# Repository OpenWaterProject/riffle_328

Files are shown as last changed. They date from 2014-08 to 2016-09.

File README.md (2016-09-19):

#Welcome!

This is a set of code and instructions for getting started with the Riffle_328 water monitor, version 0.1.8. 

- **QUICK START**.   If you already have experience using Arduino-compatible boards, you should probably just jump to the [Quick Start](https://github.com/dwblair/Riffle-Getting-Started#quick-start) section below to get up and running quickly. In general, the Riffle behaves like an Arduino UNO in the Arduino IDE (you should select "Arduino UNO" as the "Board" in the IDE), but you'll need to install a **special driver** (see [Software prep](test), below) in order to program the device over USB if you're using Mac or Windows.  

- **STEP-BY-STEP**.  If you would prefer more detailed instructions for setting up your Riffle, please check out the [Step-by-Step Instructions](./step-by-step.markdown).

- **EXAMPLES**. If you'd like to try out some example Riffle sensor applications (temperature, pressure, etc) in the [wiki](https://github.com/dwblair/Riffle-Getting-Started/wiki) of this repository (add your own!).

- **DESIGN PHILOSOPHY**.  A brief description of the motivation behind the design of the Riffle can be found [here](https://github.com/OpenWaterProject/riffle/blob/master/design_philosophy.md).  

# How you can contribute

Some useful guidelines about the best way to contribute to the project (or to fork it) can be found [here](contributing.md).

# Support and Licensing 

The Riffle_328 project has been supported through [Public Lab](www.publiclab.org)'s Open Water Initiative, and is licensed under [CERN OHL 1.2](LiCENSE.md).

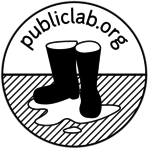
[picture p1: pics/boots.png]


# Quick Overview

**Hardware notes**.  This repository contains the design files and Bill of Materials for the Riffle water monitor.  The Riffle_328 is directly compatible with the Arduino IDE (it can be programmed as an "Arduino UNO" board).  The Riffle_328 ver 0.1.8 has the following features:

- Programmed as an "UNO" in the Arduino IDE
- Uses an Atmel 328p chip, running at 16 MHz and 3.3V.
- On-board microSD card
- On-board Serial-USB conversion using the CH340 chip.
- Battery measurement circuit
- High-precision, temperature-compensated RTC, the DS3221, with a CR1220 backup battery to maintain the time.
- Two power inputs, 3.5 - 6V.  -- one allows for Lithium-Ion charging when the Riffle is plugged into USB, the other is for extended, low-power operation. 
- It has additional on-board EEPROM memory, accessible via the I2C bus.
- It has MOSFET switches that can power down the microSD card, the external sensor power, and the battery measurement circuitry. 
- Analog pins, Digital pins, Power, Ground, Battery voltage, and I2C and SPI buses are broken out on a 2x7 header at the end of the board, as follows:

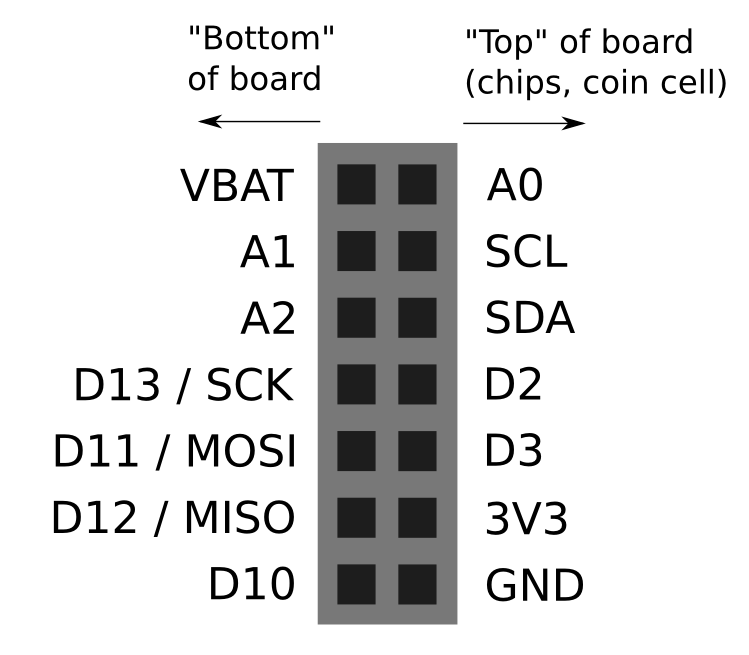
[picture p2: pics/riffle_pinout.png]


**Versions of the Riffle**. [Ben Gamari](https://github.com/bgamari)'s original [Riffle design](https://github.com/bgamari/riffle) is based on an ARM Cortex-M4 chip, the Kinetis K20.  The K20 is a more powerful chip than the Atmel 328, but the K20 version of the Riffle doesn't currently have firmware compatible with the Arduino IDE.  The Riffle_328 design covered in this repository is intended to be as directly compatible with the Arduino IDE as possible.

**Finding more resources**. The Riffle has been developed through many contributions by members of the [Public Lab](http://publiclab.org) community.  For more information, see:

- The main [Public Lab Riffle wiki](https://publiclab.org/wiki/riffle);
- All [posts and research notes](https://publiclab.org/search/riffle) related to the Riffle on Public Lab;
- The [Public Lab Water Quality Mailing list](https://groups.google.com/forum/#!forum/plots-waterquality).

# Quick Start

## Hardware prep

- For basic datalogging, ou'll need a Riffle board, a 3-6 volt battery (3.7 V Lithium Ion battery shown), and CR1220 coin cell battery.  Protoboards (shown) are optional. 

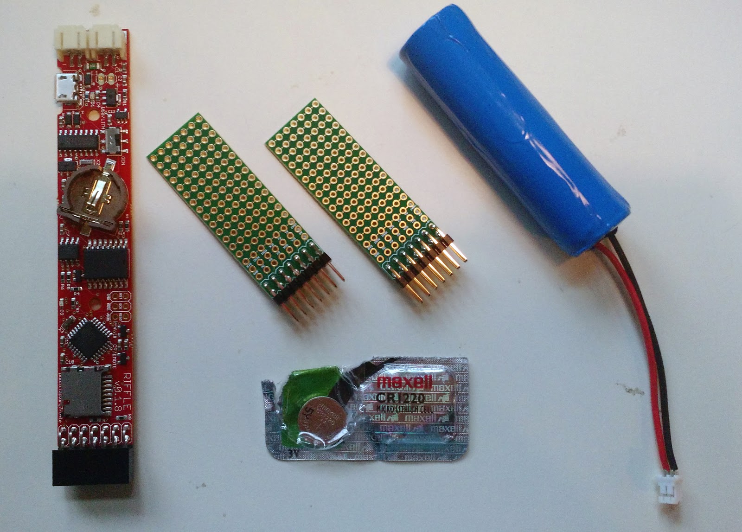
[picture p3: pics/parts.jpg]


- Insert a microSD card and a CR1220 coin cell into the appropriate slots on the Riffle.

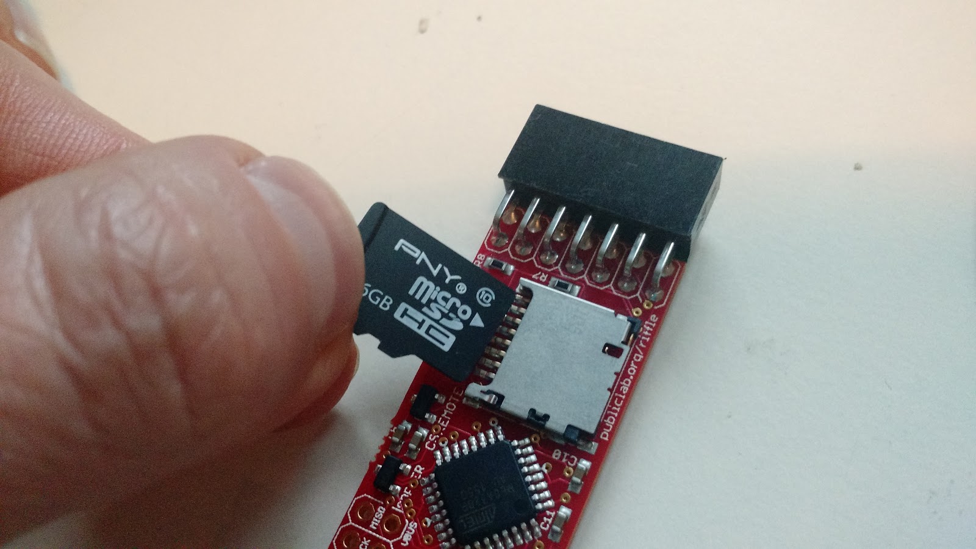
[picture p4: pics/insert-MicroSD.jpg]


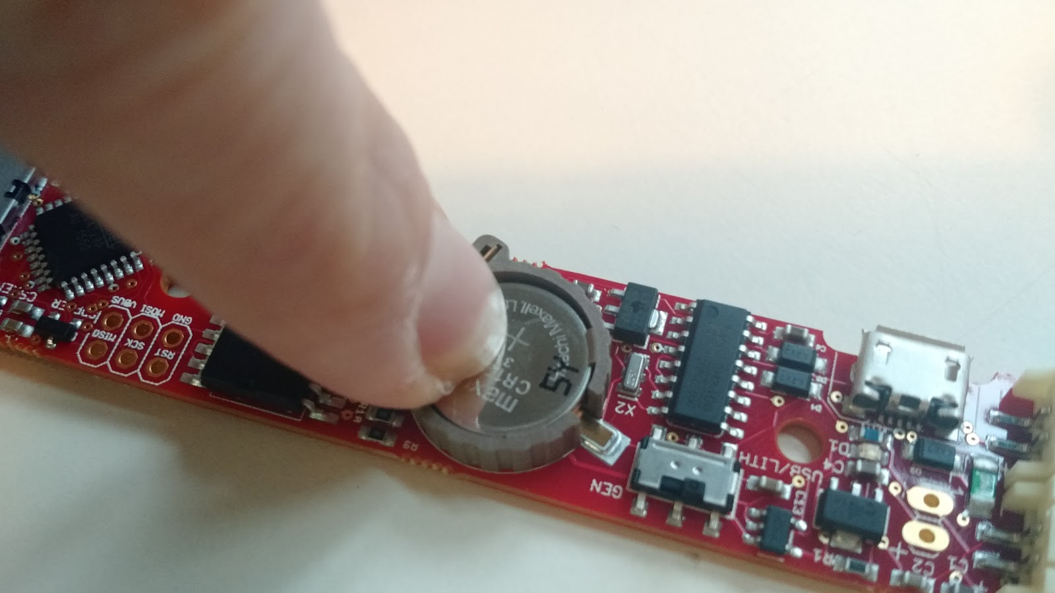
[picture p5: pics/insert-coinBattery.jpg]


- The Riffle 328 ver 0.1.8 has two JST connectors for power inputs, a switch to choose between the two power inputs, and an indicator LED in the middle of the board (connected to pin 9):

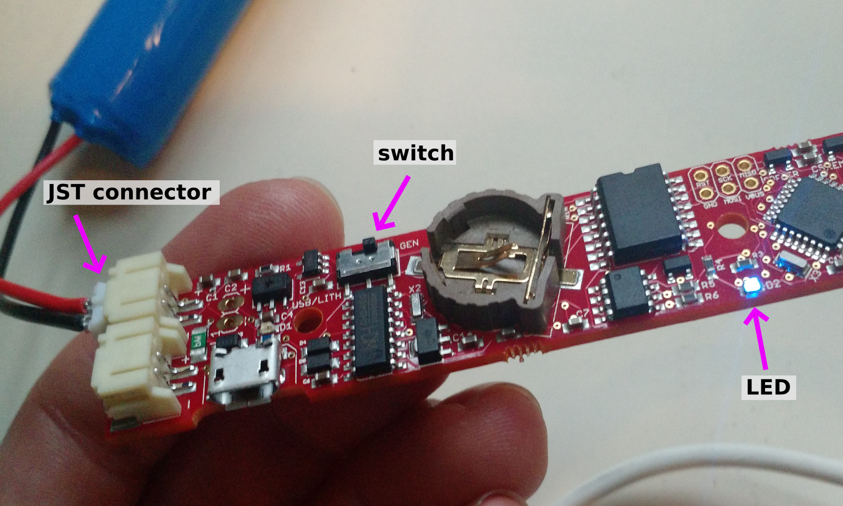
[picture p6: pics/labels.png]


- Insert a lithium ion battery into the 'Lith/USB' JST connector (JST connector labels are on the back side of the board).

- Make sure that the switch on the Riffle is switched to the side labeled 'Lith/USB' (label is next to switch).

- When you're done, your setup should look like this:

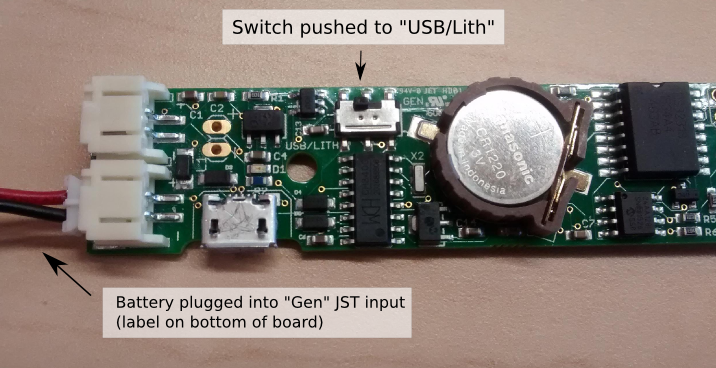
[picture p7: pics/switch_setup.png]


## Software prep

- Make sure that the Arduino IDE (version 1.6.10 or higher) is installed.  If it
 isn't, get it [here](https://www.arduino.cc/en/Main/Software).

- **Installing the USB-Serial Driver**. On Mac or Windows, the Riffle requires a special driver in order to be programmed via the Arduino IDE, due to the onbaord CH340 USB-Serial chip.  For Windows, you can use the driver [here]( http://raysfiles.com/drivers/ch341ser.exe).  For Mac, follow instructions [here]( http://www.instructables.com/id/Arduino-Nano-CH340/). Linux systems should generally not require additional drivers.

- Copy all of the folders in 'arduino_libraries' into the 'libraries' folder inside the 'sketchbook' folder associated with the Arduino IDE install.  These libraries are necessary for running the 'temp_logger.ino' and 'set_rtc.ino' sketches in this repo.  

## Logging values to the microSD card

- Using the Arduino IDE, compile the 'temp_logger.ino' code from the "example_sketches" folder in this repo, and load it onto the Riffle board, using 'Arduino UNO' as the 'Board' version in the Arduino IDE.

- The Riffle should start logging temperature values to the microSD card. These temperature values come from the on-board RTC, and so may be affected by the temeprature of the board (which might slightly higher than ambient temperature, due to the operation of its circuitry). 

- Note: the RTC will have its time set automatically to the system clock when it is programmed via the Arduino IDE.

## Extending the battery lifetime

- Set DEBUG = 0 in temp_logger.ino. This will reduce power by turning off the Serial interface.  It will also mean that the RTC is not set by the System clock.

- Use the 'GEN' JST connector on the Riffle board.  This power input doesn't have a protective diode, thus avoiding a diode-associated voltage drop, and can power the Riffle down to lower battery voltages.

- Test out different microSD cards;  some of them 'sleep' at lower power settings than others.

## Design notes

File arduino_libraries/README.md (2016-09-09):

# Required Arduino Libraries

These libraries must be placed in the 'libraries' folder of your Arduino sketchbook folder.

**Note**:  this snapshot of the libraries is known to work with Riffle 0.1.8.

If you'd like to try updated versions of the libraries (or contribute to bug fixes / development), visit to original libraries below:

- [SdFat](https://github.com/greiman/SdFat)
- [EnableInterrupt](https://github.com/GreyGnome/EnableInterrupt)
- [DS3231](https://github.com/kinasmith/DS3231)
- [LowPower](https://github.com/rocketscream/Low-Power)

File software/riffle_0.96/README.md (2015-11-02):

# Riffle v0.96 Software

Here is the software for the Riffle board version 0.96, which is the production board for the summer of 2015.

## Requirements

### Power Up

The Riffle's brain needs to be on to interact with it. (The "power" led just means there's power to the board, not necessarily that the brain is on. Just slide the switch toward the edge of the board to turn it on.

### Arduino Libraries

The Riffle's Real Time Clock needs a particular flavor of the RTC libarary to be in your Arduino's "Library" folder, which comes via [mizraith's Github page](https://github.com/mizraith/RTClib). Here's what to do:

  - [Download this zip file](https://github.com/mizraith/RTClib/archive/master.zip)
  - Unzip it
  - Remove the "-master" from the folder name so it's "RTClib" instead of "RTClib-master"
  - Move that whole folder into your Arduino "libraries" folder. ([Here is more information](https://learn.sparkfun.com/tutorials/installing-an-arduino-library) on doing that, if you need it.)
  - Restart your Arduino software (also known as the Ardunio IDE).

### USB Driver

The Riffle is using a special USB chip, and may require a special driver so that it is recognized by your computer.

#### Mac OS

For Macs, you'll definitely need a driver. Download and install it from here: [http://raysfiles.com/drivers/ch341ser_mac.zip](http://raysfiles.com/drivers/ch341ser_mac.zip)

#### Ubuntu

If you're using Ubuntu, you don't need anything special.

## Arduino Setup

- Lie to your Arduino software and tell it that Riffle is an "Arduino Uno" in the `Tools > Board` menu.

### Mac OS

- Under `Tools > Serial Port` pick the thing that looks most like: `/dev/tty.wchusbserialXXXX`

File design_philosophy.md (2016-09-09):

# Problem definition
- HOBO datalogger used widely; YSI
- Costs
- Want something extensible
- Something that can connect to the hobby electronics movement
- Use existing code with minimal fuss / muss
- Wanted to make it easy to deploy -- pvc, water bottle, some easy and cheap enclosure
- Easy to share data -- sd card

# Form factor and enclosure
- Wanted to enable water bottle as ‘easiest option’
- Also allows for thin PVC

https://publiclab.org/notes/mathew/02-26-2015/sensors-in-soda-bottles
https://publiclab.org/notes/mathew/01-16-2015/sketching-a-waterproof-pop-bottle-sensor-system

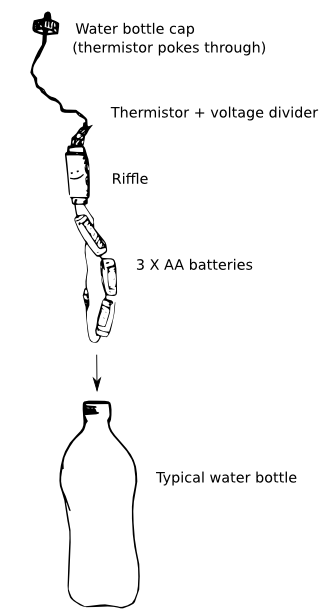
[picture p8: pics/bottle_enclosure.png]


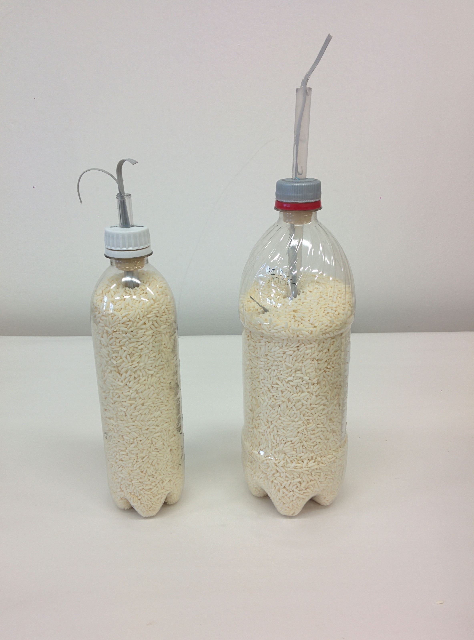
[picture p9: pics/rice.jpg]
 

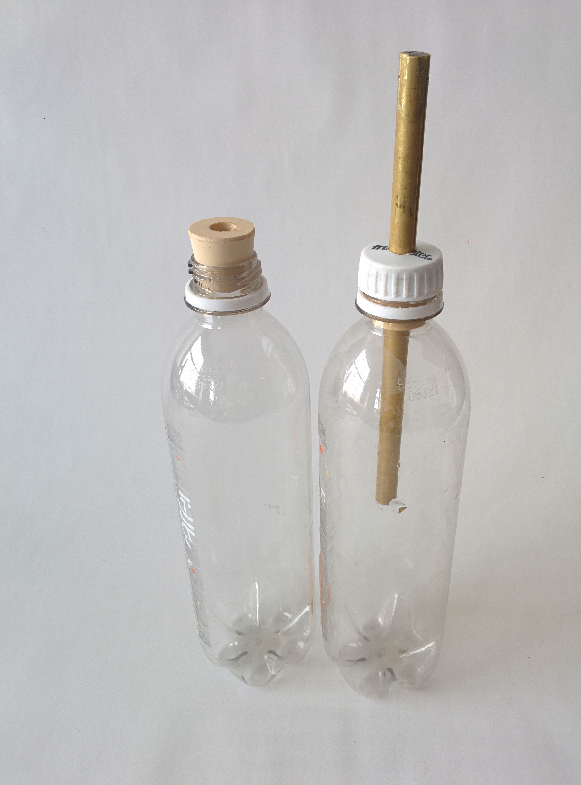
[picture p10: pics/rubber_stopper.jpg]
 

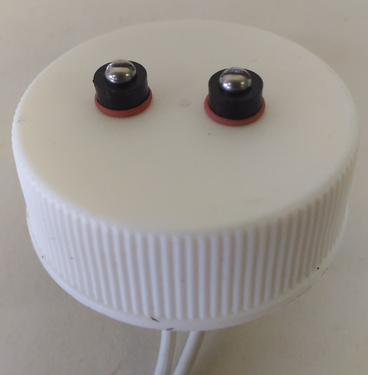
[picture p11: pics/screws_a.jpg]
 

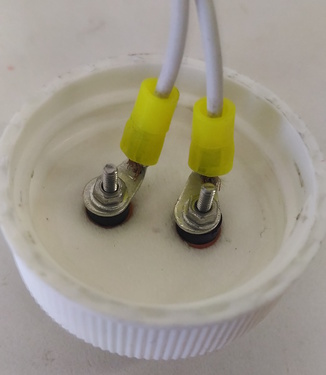
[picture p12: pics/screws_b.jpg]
 

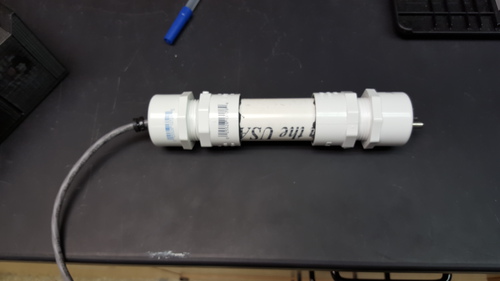
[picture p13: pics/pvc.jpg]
 

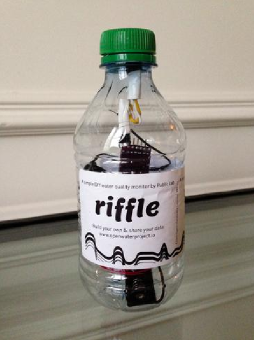
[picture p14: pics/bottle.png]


# What drove IC / placement choices
- Atmel vs ARM
- CH340 -- cheap and easy (but not easy to source)
- DS3231 -- want temp-compensated RTC to line up timestamps
- 2x7 header at end -- to allow water bottle config
- SPI and I2C breakouts at end 
- Hardware interrupts D2 and D3 for any related applications (freq-based measurements like conductivity and depth)
- EEPROM for storing configurations
- Mounting holes for gen purpose mounting

# Power management / choices
- Battery charging circuit
- But requires protective diode to allow for disconnect from USB Serial chip
- So, want to avoid voltage drop
- So, create “gen” battery input, without diode / voltage drop
- RTC alarm functionality 
- Want very low power -- mosfet on external board, mosfet on SD card, mosfet on battery measurement

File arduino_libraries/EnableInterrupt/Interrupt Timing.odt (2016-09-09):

Pin Change Interrupt Timing

an exploration of latency and design

by: GreyGnome (aka, Mike Schwager)

Feb. 8, 2015 v. 1.0

# Introduction

I have a "dirty" switch: it bounces a lot when pressed. The bounces can occur very quickly, on the order of only microseconds apart. This switch is attached to an Arduino Duemilanove, based on the ATmega328p processor. The pin change interrupts on the ATmega chips act only on change of signal (either rising or falling), and they trigger when any pin on a port (== up to 8 pins) is triggered. If you want to determine which pin actually triggered, that would take software and that means a delay from the moment of signal change to determining which pin triggered the change. With a pin change interrupt enabled to trigger on the pin's port, how will a library designed for general use- which must use an algorithm to find the proper pin- react when this switch is pressed?

It bears repeating that for Pin Change Interrupts, the interrupt can take place when any pin on the port is interrupted. This presents a serious design challenge. If you have the luxury of knowing at the time of the signal which pin interrupted, you can design fast, custom code that will react to your simple situation. But remember that we are talking about a library: we don't know which pin may be doing the interrupting. So it must survey the pins to figure out which one(s) changed and had triggered the interrupt. Furthermore, there is an appreciable amount of time that it takes from the moment the triggering event happened to when we enter the interrupt subroutine (ISR) and go through the logic to figure out which pin did the triggering. ...How much time? That I aim to find out.

Why is this a big deal? Think of a bouncy switch: the interrupt triggers, the ISR starts up,

and the first thing we need to do is query the port to see the state of its pins. Well, some time

has elapsed since the triggering event and the query. In the course of that time, it's entirely

possible- and I'm writing this because it's not only possible, but it can happen quite readily-

that the state of the pin changes before we get a chance to sample it. So we get an interrupt but

it looks like a false alarm! The ISR never calls the user's function because none of the user's

interrupt pins appear to have changed.

# The Delay

There is no complete solution to this problem, because of the nature of Pin Change Interrupts and the nature of a general purpose Interrupt SubRoutine (ISR). All you can do is mitigate the situation. I will attempt to do so by capturing the state of the port as early as possible in the ISR. The question is, how early is that?

No matter what, it will take some number of machine instructions from the time of the signal to actually executing the ISR: The current instruction is completed, and there is a jump to the ISR code which takes 3 clock cycles. So that's at least 4 clock cycles, which is about 250 nanoseconds on a 16MHz machine (4 * 62.5 ns). Best theoretical case, then, is that after our signal triggers an interrupt it will take us 250 ns to sample the pin's state. But there's much more than this.

## A General-Purpose ISR Must Save Registers

An interrupt is by definition asynchronous- the computer never knows when it's going to happen. And the compiler writers are not able to know the myriad types of logic that will be necessary inside an interrupt. Thus they can never know which registers may be necessary for a user's ISR, and the implications of that are pretty significant. It means that the first thing the ISR should do is save the values of each and every register of the CPU. ...But isn't that expensive, time-wise? Why yes, yes it is. How so? Here is what the assembly looks like at the beginning of a compiler-generated ISR; note the proper preamble to the ISR pushes all registers (there are reasons registers r2-r17 are not saved for reasons that are not clear to me, but the assembly generated by the compiler for the ISR doesn't use them):

ISR(PORTC_VECT) {

292: 1f 92 push r1

294: 0f 92 push r0

296: 0f b6 in r0, 0x3f ; 63

298: 0f 92 push r0

29a: 11 24 eor r1, r1

29c: 2f 93 push r18

29e: 3f 93 push r19

2a0: 4f 93 push r20

2a2: 5f 93 push r21

2a4: 6f 93 push r22

2a6: 7f 93 push r23

2a8: 8f 93 push r24

2aa: 9f 93 push r25

2ac: af 93 push r26

2ae: bf 93 push r27

2b0: cf 93 push r28

2b2: df 93 push r29

2b4: ef 93 push r30

2b6: ff 93 push r31

The ISR can make no assumptions: What was the state of the CPU when the interrupt took place? What registers are in use by a user's function when called from within the ISR? The compiler is pretty sophisticated, but to ask it to optimize so as to follow a trail of function calls so as to shorten an ISR preamble is beyond its capabilities.

The trouble is in the ISR's function call. In order to allow the library to accept a function call like

enableInterrupt(Pin, function, mode);

where the function's name may not be known at compile time, the ISR must be ready for any eventuality. To not do so means risking bugs by not preserving the main program's registers.

## A Small ISR, for Comparison

So we need our massive preamble. What about an ISR that does not have such restrictions? What if our ISR was simple, and its needs were known to the compiler? To see, I create a small ISR in C:

volatile uint8_t pinstate;

ISR(PORTC_VECT) {

pinstate=PINC;

}

This ISR simply copies the state of Port C to the volatile pinstate variable, which is a memory address accessible by the main program or any function in our sketch. Here is the assembly language that the compiler generates from this C:

volatile uint8_t pinstate;

ISR(PORTC_VECT) {

212: 1f 92 push r1

214: 0f 92 push r0

216: 0f b6 in r0, 0x3f ; 63

218: 0f 92 push r0

21a: 11 24 eor r1, r1

21c: 8f 93 push r24

pinstate=PINC;

21e: 86 b1 in r24, 0x06 ; 6

220: 80 93 60 01 sts 0x0160, r24

}

224: 8f 91 pop r24

226: 0f 90 pop r0

228: 0f be out 0x3f, r0 ; 63

22a: 0f 90 pop r0

22c: 1f 90 pop r1

22e: 18 95 reti

Note that it's much shorter, especially the preamble and the postamble. Much of the code is there because of ISR boilerplate actions:

push r1 Save whatever may be in r1

push r0 Save whatever may be in r0

in r0, 0x3f Store SREG into r0

push r0 Save r0

eor r1, r1 Xor r1 with itself, which is a clever way to put '0'
in r1

How efficient is it? Well we don't need SREG, because the read of port C: in r24, 0x06, and the store of it in memory using the sts 0x0160, r24 don't modify SREG. We don't need to zero out r1, because we never use r1. So all the push'ing and pop'ing are useless in this case, and serve merely to slow us down. Such is life with a compiler vs. hand crafted assembly code. It may be useful to create a hand-crafted ISR in this case.

# Testing Speed

## Entering the ISR

I attempt a test:

A switch is connected as follows: A pin is configured as an input port, and the pullup resistor is on. Pin Change Interrupt is enabled on the pin (which will trigger on any level change). So when I press the switch, the signal goes from high to low and the interrupt is triggered.

My ISR looks (in part) like this; this will turn on and off the Arduino Uno's pin 13 LED:

ISR(PORTC_VECT, ISR_NAKED) {

uint8_t interruptMask;

uint8_t ledon, ledoff;

ledon=0b00100000; ledoff=0b0;

PORTB=ledoff; // LOW

PORTB=ledon; // HIGH

PORTB=ledoff; // LOW

PORTB=ledon; // HIGH

PORTB=ledoff; // LOW

(...)

}

The generated assembly code looks like this:

00000292 <__vector_4>:

ledon=0b00100000; ledoff=0b0;

PORTB=ledoff; // LOW

292: 15 b8 out 0x05, r1 ; 5

PORTB=ledon; // HIGH

294: 80 e2 ldi r24, 0x20 ; 32

296: 85 b9 out 0x05, r24 ; 5

PORTB=ledoff; // LOW

298: 15 b8 out 0x05, r1 ; 5

PORTB=ledon; // HIGH

29a: 85 b9 out 0x05, r24 ; 5

PORTB=ledoff; // LOW

29c: 15 b8 out 0x05, r1 ; 5

Notice a little optimization here: r1 is defined to always contain 0, so we don't even have to load

a value from memory (0 is an important number!). This makes the first out 0x05, r1 command very quick, and by using an oscilloscope we can see just how quickly the chip reacts after receiving the signal:

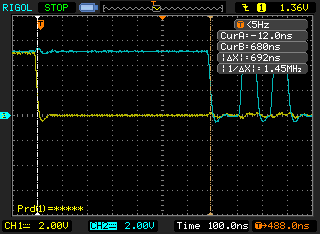
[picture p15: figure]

'.

Look at the two vertical lines on the left and center-right in the above screenshot- those are the cursors. ...So we are measuring 700 nanoseconds from when my switch first closed its connection (yellow trace) to where pin 13 went LOW (blue trace). The cursor lines tell the tale.

How much of that 700 nanoseconds was taken up by the first command itself, the one that signals pin 13? That is:

292: 15 b8 out 0x05, r1 ; 5

In the blue trace, you can see that after I go low I go high, then low, then high again. The second dip- the shorter dip- above, should tell the tale. And it says:

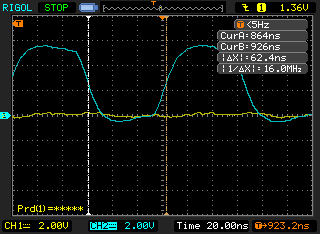
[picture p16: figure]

(note that here I have zoomed in for a closer, more accurate look)

...Lo and behold, the trough- the PORTB=ledoff; is 62.4ns wide, which is equivalent to a 16.0MHz frequency, which is a single clock cycle of the ATmega328p. Note that the data sheet states that the OUT assembly instruction takes 1 cycle. Yay, the stars align!

Now- going back to the first picture: How long did it take to enter the ISR? My experiment measures the time from the switch close to the Pin13 going LOW. We can subtract the time to execute that first command, and get to exactly how long it takes us to enter the ISR:

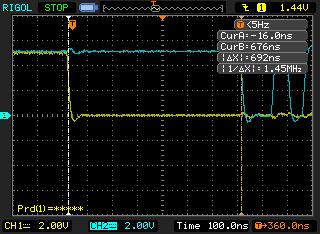
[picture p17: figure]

...That's 692ns measured, or approximately 11 cycles. Minus the 1 cycle that it took our command to run, it takes 10 cycles' time from interrupt to entering the ISR.

Thus, the best response to an interrupt that we could ever hope for is 630ns, more or less. That's at least 630 ns between activation and having a ghost of a chance to query the pins and store their value.

## The Preamble

BUT! Can we just stuff an “in” command at the beginning of the ISR, in order to grab the port's pins' values? Remember, this is a general purpose ISR so the compiler inserts a preamble and a postamble. Here is what the assembly looks like when we don't use NAKED_ISR; note the proper preamble to the ISR (there are reasons registers r2-r17 are not saved; suffice it to say they are scratch and their values are not guaranteed):

ISR(PORTC_VECT) {

292: 1f 92 push r1

294: 0f 92 push r0

296: 0f b6 in r0, 0x3f ; 63

298: 0f 92 push r0

29a: 11 24 eor r1, r1

29c: 2f 93 push r18

29e: 3f 93 push r19

2a0: 4f 93 push r20

2a2: 5f 93 push r21

2a4: 6f 93 push r22

2a6: 7f 93 push r23

2a8: 8f 93 push r24

2aa: 9f 93 push r25

2ac: af 93 push r26

2ae: bf 93 push r27

2b0: cf 93 push r28

2b2: df 93 push r29

2b4: ef 93 push r30

2b6: ff 93 push r31

uint8_t ledon, ledoff;

ledon=0b00100000; ledoff=0b0;

PORTB=ledoff; // LOW

2b8: 15 b8 out 0x05, r1 ; 5

Now let's measure the time from interrupt to shutting off the Pin 13 LED again in that out 0x05, r1 command, just like before. It's given here:

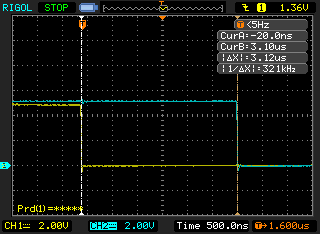
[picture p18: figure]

...yikes! 3.12 microseconds! That's 50 times as long as 62.5 nanoseconds... which means, 50 machine cycles! Well, we do have 17 “push” instructions alone- at 2 cycles each, that's 32 * 62.5ns right there.

This means it would be 3.12 microseconds- at least- from a triggering event, to querying the pins of the PORT, to see which pin triggered. That's painful. Is there anything we can do?

## Query the Port by Hand

There is something: by hand-coding the preamble and post-amble, grab the contents of the port as soon as possible. Here's the code:

ISR(PORTC_VECT, ISR_NAKED) {

uint8_t current;

uint8_t ledon, ledoff;

ledon=0b00100000; ledoff=0b0;

asm volatile("\t"

"push %0" "\t\n\t"

"in %0,%1" "\t\n\t"

: "=&r" (current)

: "I" (_SFR_IO_ADDR(PINC))

);

PORTB=ledoff; // LOW

// in r0, __SREG__ instruction saves SREG, then it's pushed onto the stack.

asm volatile(

"push r1" "\n\t"

"push r0" "\n\t"

"in r0, __SREG__" "\n\t" // 0x3f

"push r0" "\n\t"

"eor r1, r1" "\n\t"

"push r18" "\n\t"

"push r19" "\n\t"

"push r20" "\n\t"

"push r22" "\n\t"

By saving our current PORT state into the variable “current” at the very start of the ISR, using assembly language, we are able to get it as quickly as practicable. Note, however, that because of an SR's special nature we can not be sure if the main code was using the register that will be used for “current” in the “%0” placeholder in the code: “in %0,%1”, above. Therefore, we must push it first... and take care to pop it last at the end of the ISR.

"push %0" "\t\n\t"

"in %0,%1" "\t\n\t"

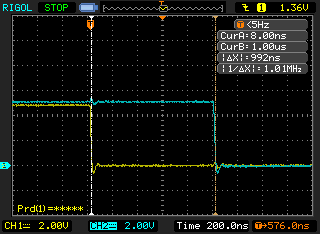
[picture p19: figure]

Now that we have captured our PORT state as soon as possible, we ask: How well did we do? The screen says it took 992 ns... that's about 300 ns slower than a naked ISR preamble, or about 5 cycles. That's close to what we would expect from the assembly code: 2 cycles for the push, 1 for the in, and 1 for the out (to make the LED line go LOW). 4 instructions, or an expected 248ns slower than the routine with the PORTB=ledoff; command first.

...But we're still 62 ns off. What gives? According to my tests, over the course of many runs, there could be some jitter in our interrupt timing. As a matter of fact, there are some significantly longer periods than the one just shown. Take this run for example:

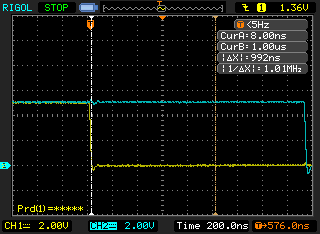
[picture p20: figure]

Here, the two cursors are in exactly the same positions as the previous screenshot.This time it took almost 800ns longer to respond to the interrupt.

This sort of thing happened infrequently, but over the course of a few runs one could find an outlier like this. My feeling is that sometimes the CPU may be in, for example, a timer interrupt and it is unable to service this interrupt until it's done. That's something to keep in mind.

Ultimately, the Pin Change Interrupts are a bit of an oddity. A single interrupt is called for any pin on a port that is triggered, and one needs software if one wants to determine which pin activated. Even then, there's no guarantee that the pin is in the same state that it was when the interrupt was triggered! Caveat programmer- you must be aware of of the capabilities of the hardware that you're working with, and of your system's own performance needs.

That said, I have used a relatively slow Pin Change Interrupt library with great success (http://code.google.com/p/arduino-pinchangeint/). Most cheap switches, for example, are quite bouncy so it's necessary to account for a certain degree of slop in the real world. This is what engineers are paid to do: Make components and systems work in the real world.

And that, my friends, is what they call Rocket Science: It ain't easy.

# A Real Life Example of a Bouncy Switch

## Tracing the Interrupts' Behavior

How well is the ISR grabbing the proper pin state on a fast-changing signal? “Fast” is relative, but for an Arduino running at 16 MHz I would say that fast is anything in the microsecond range. The Arduino's clock runs at a period of 62.5ns which is one machine instruction. In the space of 1 microsecond 16 (1-cycle) machine instructions can run... that's not a whole lot.

In this test, the interrupt library does the following:

1. As soon as we've saved the current PORT state, send out a single pulse.
2. As soon as we've found the pin that on the port that we believe triggered the interrupt, send out a double pulse.

The interesting code parts are these:

ISR(PORTC_VECT, ISR_NAKED) {

uint8_t current;

uint8_t i;

uint8_t interruptMask;

uint8_t ledon, ledoff;

ledon=0b00100000; ledoff=0b0;

asm volatile("\t"

"push %0" "\t\n\t"

"in %0,%1" "\t\n\t"

: "=&r" (current)

: "I" (_SFR_IO_ADDR(PINC))

);

PORTB=ledoff; // LOW

PORTB=ledon; // HIGH

Then:

if (interruptMask & 0x01) {

PORTB=ledoff; // LOW

PORTB=ledon; // HIGH

PORTB=ledoff; // LOW

PORTB=ledon; // HIGH

Now we can see when the interrupt triggers and when it thinks the pin state has changed. How does this line up against our bouncy switch? Are we properly reacting to all the activations?

Here is a real oscilloscope trace of a bouncy switch and of the Interrupt library reacting:

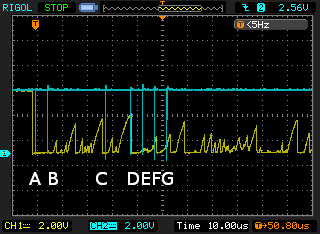
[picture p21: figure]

In this trace, the actions taken by the interrupt library are labelled A through G, in order to easily follow the sequence of events.

Note, again, that this trace shows that the real world is a dirty dirty place. Inside the processor we can be very deterministic, but in the world we have to be aware of what we are dealing with in order to design our systems properly. Here you can see the the bounces are coming microseconds apart; the X-axis time divisions are 10 microseconds. There are some significant pulses that appear less than 10 microseconds apart.

So let's evaluate the actions of the switch and the interrupt library, using that screenshot as our guide...

## Pulses A and B

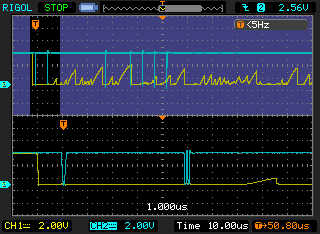
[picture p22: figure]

Zooming in on the two pulses, we see the library behave as expected: The switch (yellow trace) triggers the interrupt (blue trace) which reacts about 1us later. Then, about 5us later, the code has determined which pin activated so if you look closely at the bottom trace you can see that it sends a double-pulse (if you can't see it, you'll just have to trust me). Oll Korrect.

At this point, we have saved the current state of the pins into the portSnapshot variable: When the interrupt activates next, we'll need to know which pin changed from this activation of the interrupt.

The pin's state is saved at a LOW level.

## Pulse C

This is interesting; Pulse C is on the left at the bottom zoomed-in view:

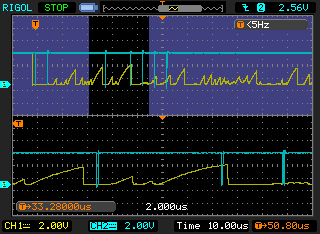
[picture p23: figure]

The interrupt is activated by the rising waveform on the left (note that the ATmega328's circuitry actually activated the interrupt somewhere inside this sawtooth). This would be a change in the pin's state, however, by the time the interrupt reacts, the pin is at a low level (refer to the leftmost pulse in the blue trace at the bottom of the above screenshot). In variable “current”, then, the pin's state is LOW. “current” and the portSnapshot variable would thus look the same, the ISR believes that no pin has activated, and there is no activation of the user's function; there is no double pulse.

Then, about 10 microseconds to the right of Pulse C, we find:

## Pulse D and E

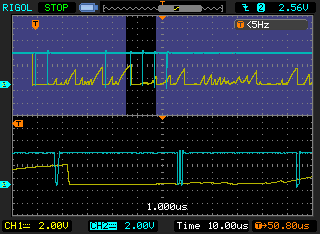
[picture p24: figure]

Pulse D is the leftmost pulse on the bottom trace in the screenshot. Here again we see an activation on a rising pulse, but this rise is appreciably longer than Pulse C. Somewhere during the rise, the ATmega328 recognizes the rising signal, the interrupt triggers, and the library captures the state of the port. This is important: because the ISR has time to recognize the HIGH level (note that the single pulse occurs while the sawtooth wave is still high, so “current” stores this HIGH level), there will be a change in the pin from what was previously saved in the “portSnapshot”. Again if you look closely you can see the double-pulse about 5 microseconds after the initial ISR pulse.

The pin change is recognized and the portSnapshot stores HIGH level.

## Pulse F and G

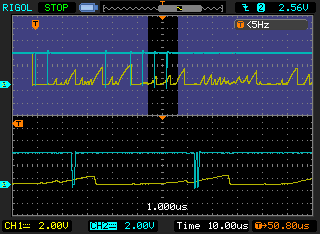
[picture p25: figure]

Here we have an interrupt seemingly out of nowhere; about 5 microseconds after Pulse E comes Pulse F, a single pulse signifying entry of the ISR again. But there is no signal (yellow trace) to activate this ISR! ...Or isn't there?

Remember that the ISR at Pulse D acted on a HIGH transition. However, very soon after the ISR's first pulse we saw the signal transition rapidly to low. The ATmega328 recognized this transition, and tripped the PCIFx register (specifically, here, it's PCIF1): it sets a flag to let the system know there is a pending interrupt. We couldn't act on the interrupt until the previous interrupt exited. However, once it did, we enter the ISR again. This was about 5 microseconds in total after executing the user's function in the previous ISR (which happens to be this:

volatile uint16_t interruptCount=0;

void interruptFunction() {

interruptCount++;

}

). All the register pop's at the end of the ISR, the return to the main program, executing a single instruction in the main program (this is guaranteed by the system), and the return to the ISR had taken 5 microseconds. Note that because the Pin Change Interrupts are high-level interrupts and there are no other interrupts set in this very simple system, we don't have to be concerned about another interrupt having used any of those 5 microseconds (see page 58 of the ATmega48A/48PA/88A/88PA/168A/168PA/328/328 datasheet).

So, to recap: During the ISR that acted on Pulse D, we flagged another interrupt due to the transition from HIGH to LOW. “portSnapshot” would have had registered HIGH for this pin, and now in the ISR for Pulse E “current” registers LOW for this pin. Thus, we find the changed pin and execute the users' interrupt routine at Pulse G.

# Implications

At the start of the Arduino sketch, prior to any switch activations, “current” shows a high value for our pin. We have seen at Pulse C that it's possible for us to miss a transition. Is it possible for us to miss a switch activation?

In the current circuit, we have essentially an RC circuit to V+ but a direct connection to ground. This would explain the sawtooth nature of the waveforms in the switch bounces:

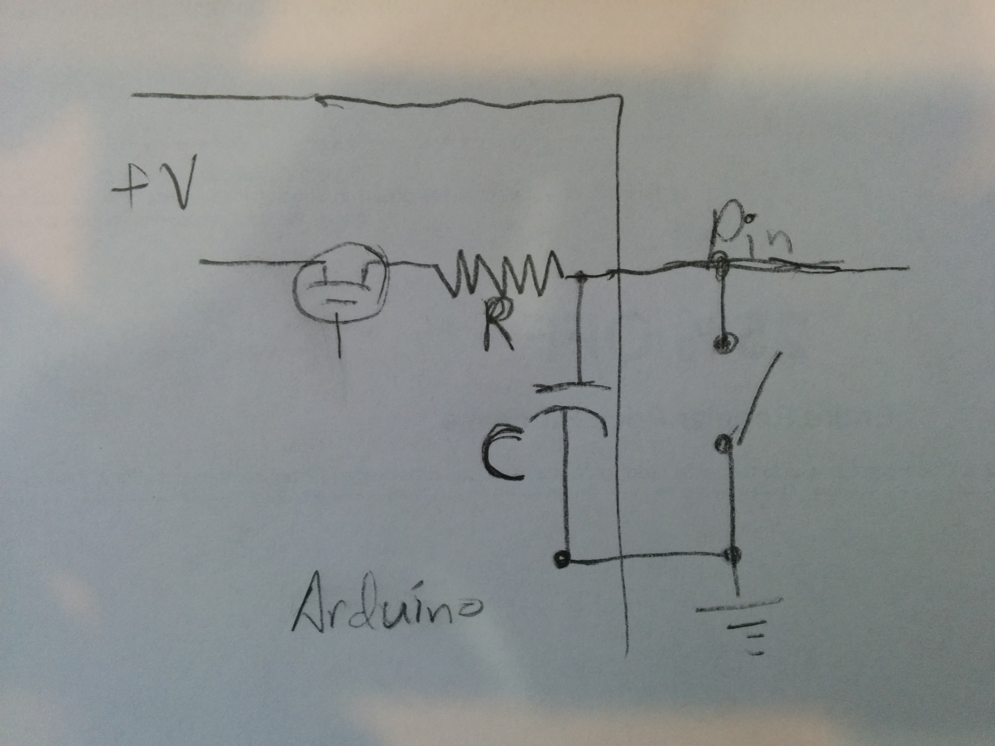
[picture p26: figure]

Because of the longer rise time of the signal when the switch is open, when the initial trigger takes place the signal goes low quickly, but it takes some time to go back to high when it bounces. So the “current” variable is likely to report LOW. So we should see the transition, and record it properly.

However there is no guarantee, and we have not even taken into consideration other interrupts that may be set. If a fast-changing signal on a pin registers a transition (on any Pin Change Interrupt pin) while an ISR is being executed, there is a good possibility that that pin's state will be misread. This makes Pin Change Interrupts a poor choice for fast-acting signals unless fault tolerance is built in to the software, and possibly even problematic in systems with a number of bouncy switches.

Again, however, multiple cheap bouncy rotary encoders have been used satisfactorily by the author with Pin Change Interrupts on the Arduino with an ATmega328p chip. The situation is not dire by any means, but again as always, Caveat Engineer; you must understand your system that is built on compromise- including, that is, the Pin Change Interrupts- and design accordingly.

# EnableInterrupt and PinChangeInt Comparison

This report was written during development of the EnableInterrupt library. The author has maintained another Pin Change Interrupt library, called PinChangeInt https://code.google.com/p/arduino-pinchangeint/. This sort of speed analysis and optimization was not performed for that library. There the compiler and system's code were accepted and measured but not criticized.

So how does this library's speed compare? Is the Enable Interrupt library a significant performance upgrade? Let's compare the two.

## Sketch

For this sketch, we're going to use a software interrupt. The idea is this:

1. Use Port C's 0-bit, which would be Pin A0 on the Arduino Uno, for the software interrupt.
2. Set A0 and Pin 13 high.
3. Print something to indicate start.
4. 2 seconds later, bring A0 low. This will interrupt the system and enter the ISR. The ISR is very simple; the function it calls is a simple variable increment.
5. However, it's a little tricky: We discover by trial-and-error that the interrupt code is not entered immediately. In the main loop, we toggle Pin 13 repeatedly. A little experimentation allows us to create exactly the series of instructions needed so that the pin LOW instruction is the last one run prior to entering the ISR. Thus we can see the LOW called jut before entering the ISR, then observe the HIGH transition performed as the first instruction after the ISR.
6. This will tell us within a couple of machine instructions' time (ie, 130 ns), the exact duration of the ISR.

Here's the loop() code:

void loop() {

uint8_t led_on, led_off; // DEBUG

led_on=0b00100000; led_off=0b0;

//*led_port|=led_mask; // LED high

PORTB=led_on;

PORTC=0x01;

Serial.println("---------------------------------------");

delay(2000); // Every 2 seconds,

PORTC=0x00; // software interrupt, port A0, triggers the ISR

PORTB=led_on;

PORTB=led_off;

PORTB=led_on;

PORTB=led_off; // at this point, we enter the ISR

PORTB=led_on; // this is after the ISR.

Here are the graphs showing the response of the system.

## EnableInterrupt

Here we see the interrupt (yellow line) and the main loop operating, until the ISR takes over and prevents the Pin 13 toggle back to on:

PORTC=0x00; // software interrupt, port A0, triggers the ISR

PORTB=led_on; // We don't see this as the pin is already HIGH

PORTB=led_off;

PORTB=led_on;

PORTB=led_off; // at this point, we enter the ISR

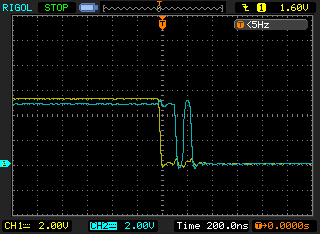
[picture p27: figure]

So it takes 4 machine instructions to enter the ISR.

Following

PORTB=led_off; // at this point, we enter the ISR

in the main loop Pin 13 is brought high again and it stays high until after the next interrupt:

PORTB=led_on; // this is after the ISR.

So we should be able to see exactly when the ISR exits and we can measure the duration of the entire ISR. Here is the graph:

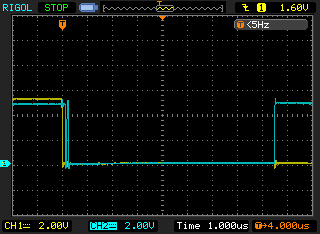
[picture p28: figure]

The ISR thus takes about 8 microseconds.

Compare the PinChangeInt library:

## PinChangeInt

It takes about the same time to enter the ISR, as expected. There is no difference between entering any ISR, that is up to the system (note that the time/div is twice as long here as the previous graph):

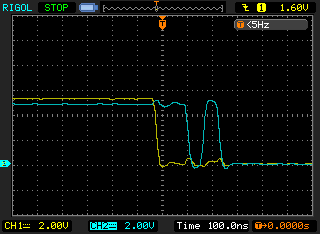
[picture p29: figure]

How long does this ISR take? The graph tells the tale:

Here we can see that, between the execution of these two commands:

PORTB=led_off; // at this point, we enter the ISR

PORTB=led_on; // this is after the ISR.

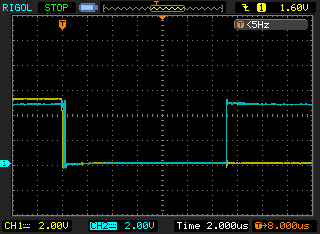
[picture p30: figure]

is about 13 microseconds elapsed time. All else being equal, the Enable Interrupt code is 5 microseconds faster.

# License

Copyright 2015 by Michael Anthony Schwager.

(http://creativecommons.org/licenses/by-sa/2.0/)
This work is licensed under a Creative Commons Attribution-ShareAlike 2.0 Generic License (http://creativecommons.org/licenses/by-sa/2.0/).

Page 12 Copyright 2015 Michael Anthony Schwager. This work is licensed under a Creative Commons Attribution-ShareAlike 2.0 Generic License (http://creativecommons.org/licenses/by-sa/2.0/)

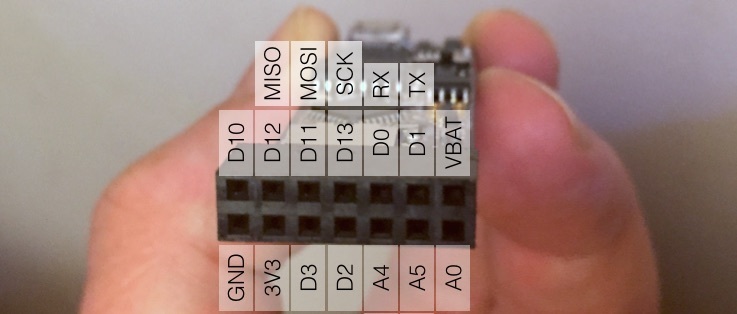
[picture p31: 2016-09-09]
pics/medium_riffle_pinouts_detail.jpg

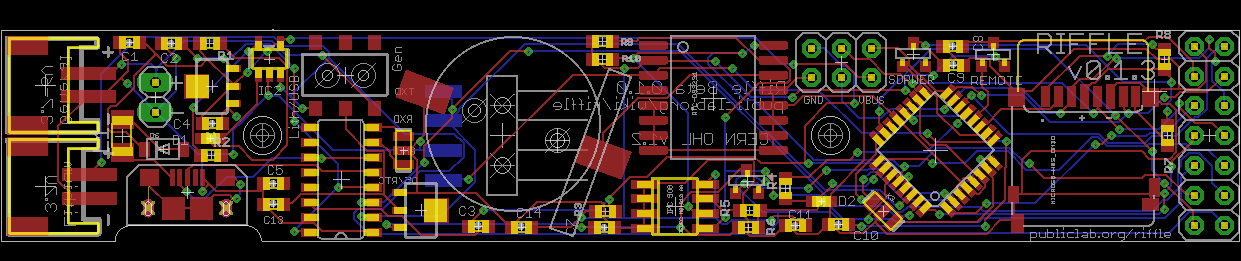
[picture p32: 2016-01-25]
hardware/riffle-beta-0.1.0/riffle-beta-0.1.3.2-board.png

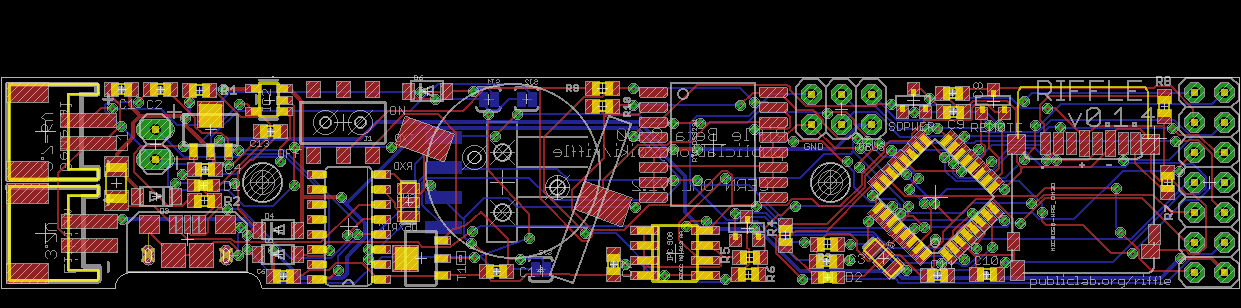
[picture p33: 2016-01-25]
hardware/riffle-beta-0.1.0/riffle-beta-0.1.7.1-board.png

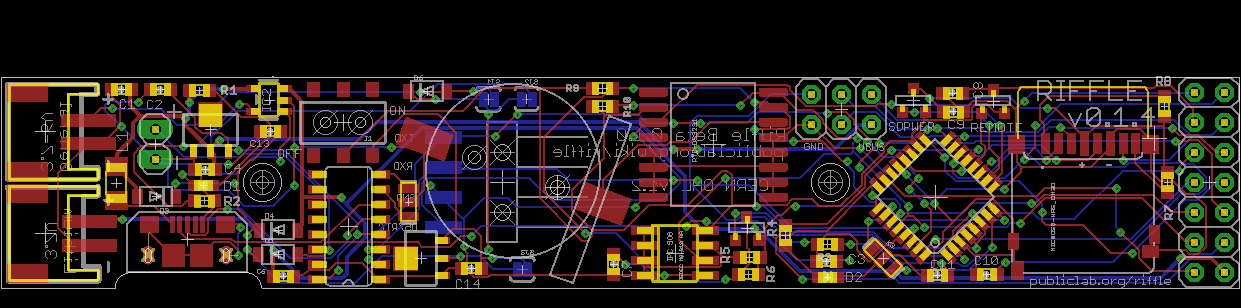
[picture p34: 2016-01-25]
hardware/riffle-beta-0.1.0/riffle-1.7.1-board.png

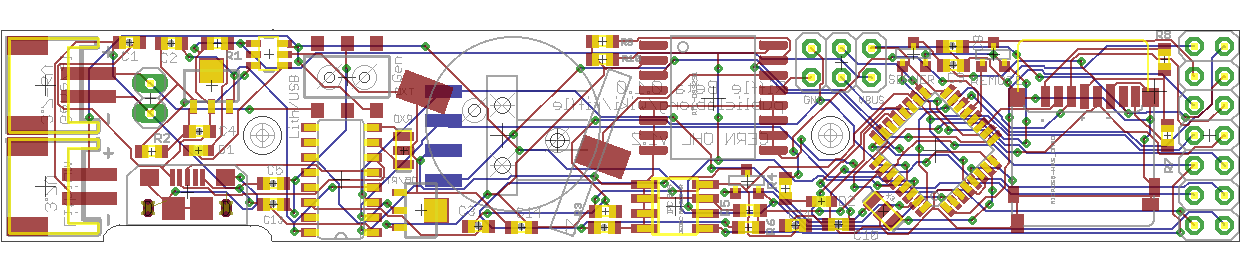
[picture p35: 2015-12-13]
hardware/riffle-beta-0.1.0/riffle-beta-0.1.0-board.png

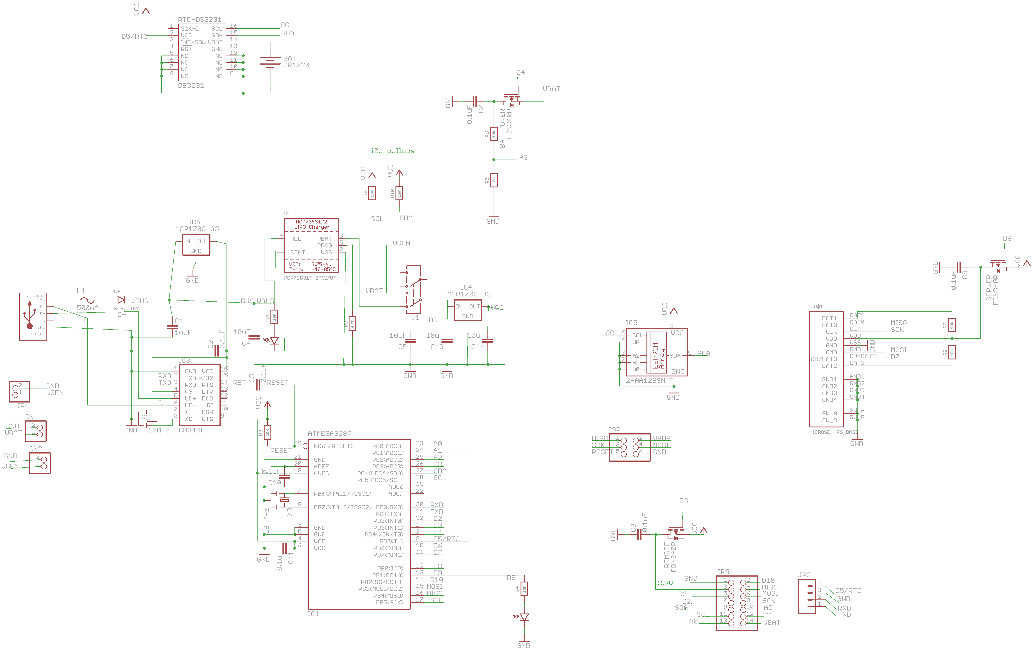
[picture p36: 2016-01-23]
hardware/riffle-beta-0.1.0/riffle-beta-0.1.3.2-schematic.png

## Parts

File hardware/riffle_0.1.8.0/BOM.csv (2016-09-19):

Part | Details | Device | Package | Description |  | MF | Cost per 100 | cost | Source
BAT | CR1220 | BATTERYBATTERY_12MM_SMT | BATTCON_12MM_SMT | Battery Holders |  |  | 1.8 | 1.8 | http://www.digikey.com/product-detail/en/1056TR/1056KCT-ND/4772075
BATTPOWER, REMOTE, SDPWER | FDN340P | PMOSSOT23 | SOT-23 | MOS FET |  |  | 0.24 | 0.72 | http://www.digikey.com/product-detail/en/FDN340P/FDN340PCT-ND/965604
C1,C4,C5,C6 | 10uF | CAP0603-CAP | 0603-CAP | Capacitor | * |  | 0.07 | 0.28 | http://www.digikey.com/product-detail/en/CC0603MRX5R5BB106/311-1448-1-ND/2833754
C2,C3,C7,C8,C9,C10,C11 | 0.1uF | CAP0603-CAP | 0603-CAP | Capacitor | * |  | 0.04 | 0.28 | http://www.digikey.com/product-detail/en/C0603C104J4RACTU/399-1097-1-ND/411372
CN1 |  | JST_2PIN-SMT-RA | JST-PH-2-SMT-RA | JST 2-Pin Connectors of various flavors |  |  | 0.4 | 0.4 | http://www.digikey.com/product-detail/en/S2B-PH-SM4-TB%28LF%29%28SN%29/455-1749-1-ND/926846
D1 | LED0603 | LED0603 | 0603-LED |  | * | blue | 0.23 | 0.23 | http://www.digikey.com/product-detail/en/APT1608QBC%2FD/754-1434-1-ND/2163792
D2 | LED0603 | LED0603 | 0603-LED |  |  | yellow | 0.17 | 0.17 | http://www.digikey.com/product-detail/en/APT1608SYCK/754-1124-1-ND/1747841
D3, D4 | SCHOTTKY | DIODE_SOD-123FL | SOD-123FL | Diode |  |  | 0.22 | 0.44 | http://www.digikey.com/product-detail/en/SM4002PL-TP/SM4002PL-TPMSCT-ND/1793404
IC1 | ATMEGA328P | MEGA8-AI | TQFP32-08 | MICROCONTROLLER | * | ATMEGA8-16AU | 2.7 | 2.7 | http://www.digikey.com/product-detail/en/ATMEGA328P-AU/ATMEGA328P-AU-ND/1832260
IC2 | MCP73831 | MCP73831 | SOT23-5 | Microchip's MCP73831 |  |  | 0.42 | 0.42 | http://www.digikey.com/product-detail/en/MCP73831T-2ACI%2FOT/MCP73831T-2ACI%2FOTCT-ND/1979802
IC3 | CH340G | CH340G | SO16 |  |  |  | 0.6 | 0.6 | rui
IC4, IC6 | MCP1700-33 | MCP1700SOT89 | SOT89 | VOLTAGE REGULATOR | * |  | 0.29 | 0.58 | http://www.digikey.com/product-detail/en/0/MCP1700T3302EMBCT-ND
IC5 | 24AA128SN | 24AA128SN | SO-08 | Serial EEPROM |  | 24AA128-I/SN | 0.5 | 0.5 | http://www.digikey.com/product-detail/en/24AA128-I%2FSN/24AA128-I%2FSN-ND/442845
ISP |  | PINHD-2X3 | 2X03 | PIN HEADER |  |  |  |  | (leave open for programming)
J1 | AYZ0202 | AYZ0202 | AYZ0202 | SPDT Slide Switch |  |  | 1.07 | 1.07 | http://www.digikey.com/product-detail/en/AYZ0202AGRLC/401-2013-1-ND/1640122
JP1 |  | PINHD-1X2 | 1X02 | PIN HEADER |  |  |  |  | (leave open)
JP3 |  | M04SMD | 1X04-SMD | Header 4 |  |  |  |  | (leave open)
JP5 |  | PINHD-2X7 | 2X07 | PIN HEADER |  |  | 0.98 | 0.98 | http://www.digikey.com/product-detail/en/PPTC072LJBN-RC/S5521-ND/775979
L1 | 500mA | PTCFUSE-1206 | R1206 | PTC fuses, resettable thermistors |  |  | 0.17 | 0.17 | http://www.digikey.com/product-detail/en/0ZCA0050FF2G/507-1480-1-ND/2165309
R1,R3,R4,R5,R6,R9,R10 | 10K | RESISTOR_0603_NOOUT | 0603-NO | Resistors | * |  | 0.02 | 0.14 | http://www.digikey.com/product-detail/en/CR0603-JW-103GLF/CR0603-JW-103GLFCT-ND/3925332
R2 | 4.7K | RESISTOR_0603_NOOUT | 0603-NO | Resistors | * |  | 0.11 | 0.11 | http://www.digikey.com/product-detail/en/MCT0603MD4701DP500/MCT0603-4.7K-MDCT-ND/2092126
R7,R8 | 50K | RESISTOR_0603_NOOUT | 0603-NO | Resistors | * |  | 0.005 | 0.01 | http://www.digikey.com/product-detail/en/RC0603JR-07100RL/311-100GRCT-ND/729644
RTC-DS3231 | DS3231 | DS3231 | DS3231 |  |  |  | 6.3 | 6.3 | http://www.digikey.com/product-detail/en/DS3231S%23/DS3231S%23-ND/1197574
U$1 | MICROSD-HRS_DM3D | MICROSD-HRS_DM3D | DM3D |  | * |  | 1.5 | 1.5 | http://www.digikey.com/product-detail/en/DM3D-SF/HR1941CT-ND/1786515
U$4 |  | USB-AB" | USB-AB-MICRO-SMD_V02_BOSS | This is a USB AB connector that is compatible with USB OTG. i.e. this connector can serve as a host or device |  |  | 0.6 | 0.6 | http://www.digikey.com/product-detail/en/10104111-0001LF/609-4053-1-ND/2350359
X2 | 12MHz | RESONATORSMD | RESONATOR-SMD | Resonator |  | X | 0.4 | 0.4 | https://www.digikey.com/product-detail/en/CSTCE12M0G55-R0/490-1197-1-ND/584634
X3 | 16 MHz | RESONATORSMD | RESONATOR-SMD | Resonator | * |  | 0.32 | 0.32 | http://www.digikey.com/product-detail/en/CSTCE16M0V53-R0/490-1198-1-ND/584635

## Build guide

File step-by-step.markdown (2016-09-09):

# Overview

This repo will cover:

- A quick [overview of the Riffle hardware](./step-by-step.markdown#riffle-hardware): switches, indicator lights, and battery ports 
- A basic ['Blink' test of the hardware](./step-by-step.markdown#basic-test-of-hardware): (does the on-board LED blink?)

As well as the required steps for setting yourself up to program a Riffle: 

- [Installing the Arduino IDE](./step-by-step.markdown#installing-the-arduino-ide) on a desktop or laptop computer
- [Installing a required driver](./step-by-step.markdown#installing-the-usb-serial-driver) for communicating between your computer and the Riffle
- A simple 'blink' test of programming capability

Finally, we cover the steps necessary for programming a Riffle to do basic datalogging:

- Downloading Riffle datalogging software from github
- Installing the required Arduino IDE libraries
- Compiling the code and loading the code onto the Riffle

# Riffle Hardware 

### Power sources

The Riffle can use power sources with voltages between 3.7 Volts and 6 Volts. 

- It can be powered via the microUSB port on the end of the Riffle. 
- It can be powered via either of the two JST ports on the end of the Riffle.  One of these ports is labeled "USB/Lith", and should only be used with a 3.7 V Lithium Ion battery.  The other is labeled "Gen", for 'general', and can be used with any voltage source (any battery chemistry) between 3.7 and 6 Volts.  

### Power switch

The power switch on the Riffle can be in two positions: 

- "USB / Lith", which draws power from the USB port and/or the "USB/Lith" JST battery port;
- "Gen", which draws power from the "Gen" battery port.

[PIC NEEDED]

Since the Riffle is only connected to one of these two power sources at a time, the switch acts as an 'on/off' switch.

### LEDs

There is an LED at the end of the board to indicated that the Riffle is plugged into USB power. [PIC NEEDED]

There is also an LED in the middle of the board.  It is connected to pin #9, and can be used as an indicator LED. [PIC NEEDED]

### MicroSD card slot

A slot for a microSD card is at the end of the board, for data storage 



### Coin cell battery slot

A coin cell battery (of type CR1220) is at the center of the board.  This coin cell is used to power the on-board real-time clock (RTC).



# Basic test of hardware: blink

The Riffle comes pre-programmed with "blink" code that blinks the indicator LED every 1 second.

- Plug the Riffle into USB power, via the microUSB port.
- Make sure that the onboard switch is set to "USB/Lith".
- You should see the Riffle blinking every 1 second or so.

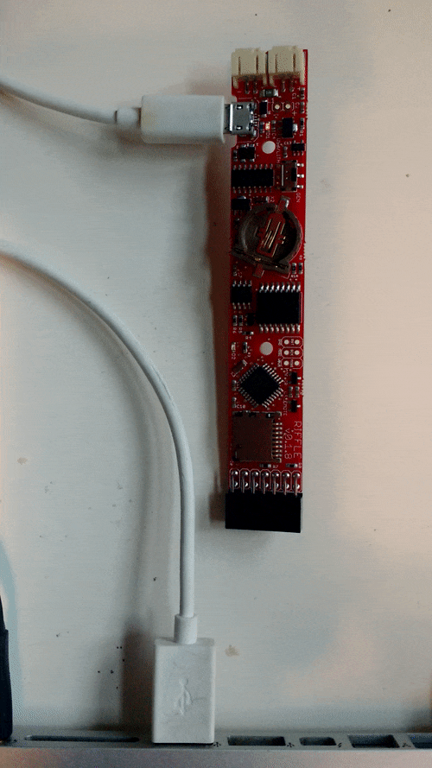
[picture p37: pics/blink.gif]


If there is no blink, check your USB power source.  If your power source seems to be okay, there may be a problem with the Riffle hardware, or it may have been programmed improperly.

# Install the Arduino IDE

- Download the Arduino IDE (version 1.6.8 or later) for your operating system (Mac, Windows, Linux) from [the arduino website](http://arduino.cc), and install it.

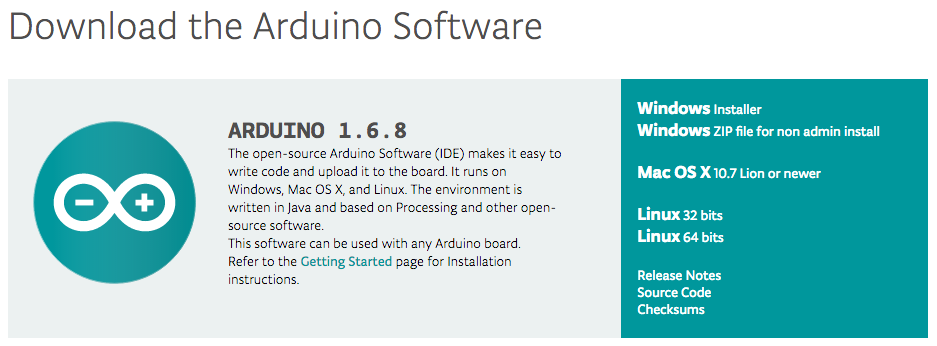
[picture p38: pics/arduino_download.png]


# Install the USB-Serial driver

The Riffle communicates with a laptop or computer via a USB-Serial chip (called the 'CH340') that requires that a special driver be installed on your computer (if you're using Mac or Windows -- no special driver required for Linux).  

### Mac

Follow the instructions [here](http://www.instructables.com/id/Arduino-Nano-CH340/) for downloading and installing the CH340 driver for Mac. The instructions link to a download to the Mac driver; we have also placed a copy of the latest driver [here](usb-serial-drivers/CH341SER_MAC.ZIP).  

Notes from people who've done this:

- Once you've downloaded the ch34xinstaller.pkg file, you'll need to unzip it -- this may happen automatically.  
- If following the Instructables linked above and downloading the driver from the linked source there, and you are running OS X Yosemite, try downloading the driver without the additional step of opening a terminal and typing in the special code, as it has worked without that step (at least for one person).

Here are some screenshots of the process:

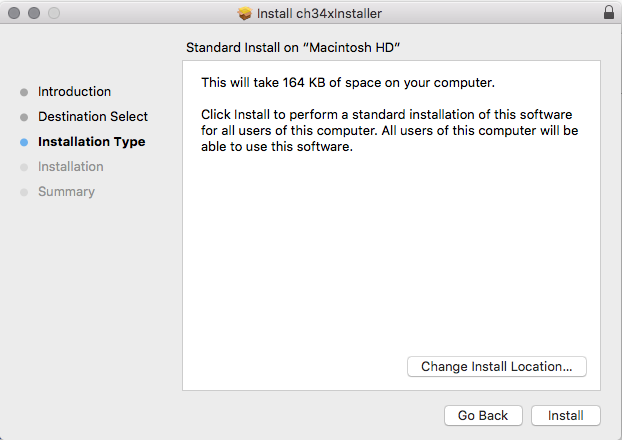
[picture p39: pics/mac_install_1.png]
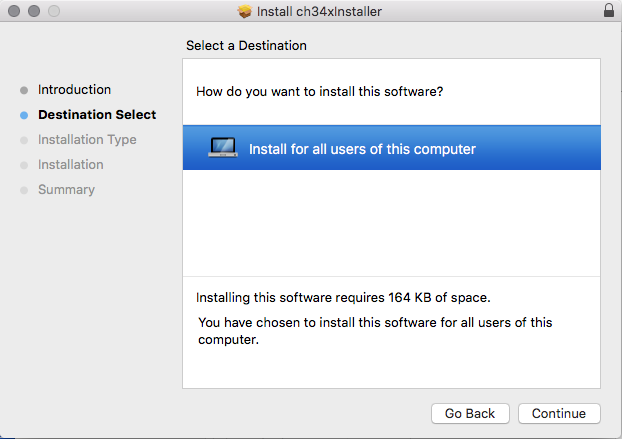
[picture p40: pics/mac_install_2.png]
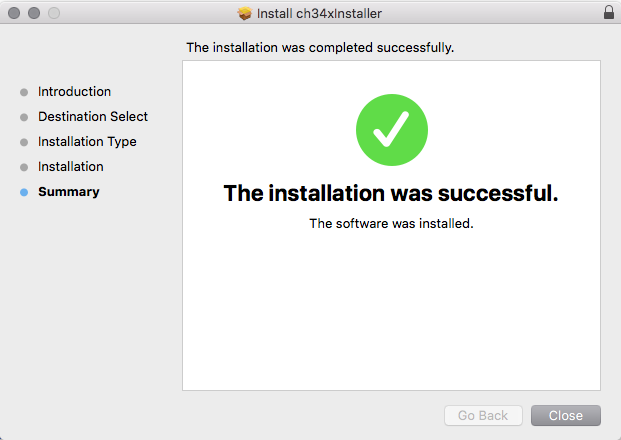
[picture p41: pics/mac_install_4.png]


### Windows

Download and install the driver [here](usb-serial-drivers/ch341ser.exe), following the prompts.

### Linux

No driver needed for Linux.

# Riffle programming basics

- Connect the Riffle to a USB port via the microUSB connector on your board.
- Make sure that the Riffle switch is set to "USB/Lith".
- Open the Arduino IDE.
- Board selection:  From the 'Tools' menu, select 'Board: Arduino/Genuino Uno'
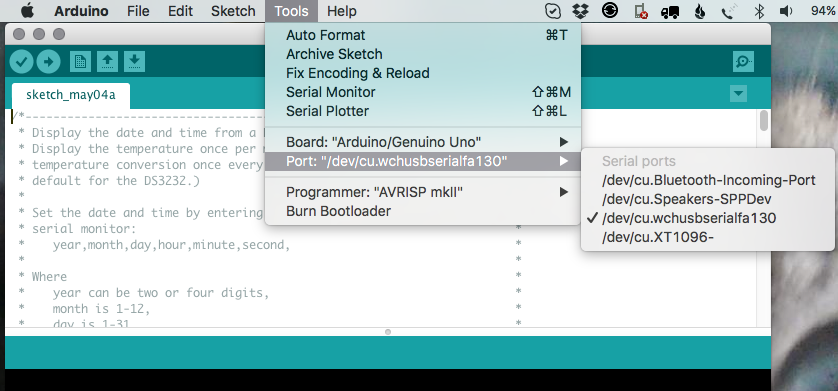
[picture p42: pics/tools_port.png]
- Port selection: in the 'Tools' menu, you must select the 'port' that the Riffle is connected to.  The precise name of this port will change depending on the operating system.  Here is a snapshot of a properly selected port on a Mac:  .  

(**Note about the usb-serial driver**:  if you are unable to locate a Riffle in the "Ports" menu, the USB-Serial driver may not have installed properly. Some people have found that restarting the computer helps.)

- Select "File: Examples: 01 Basics: Blink"

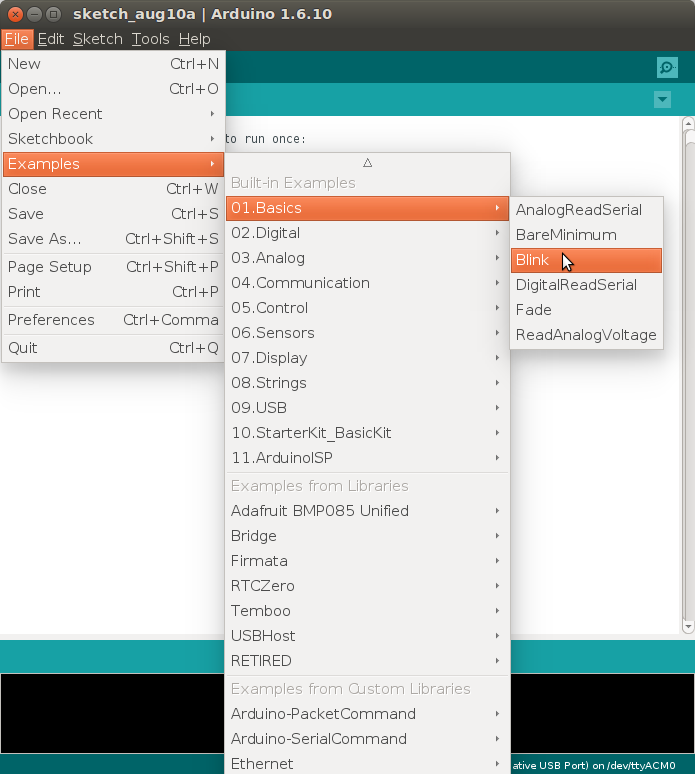
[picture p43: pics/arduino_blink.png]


- Edit every instance of '13' to '9' in the code.  (The standard Arduino UNO has its indicator LED connected to pin 13; on the Riffle it is connected to pin 9). 
 
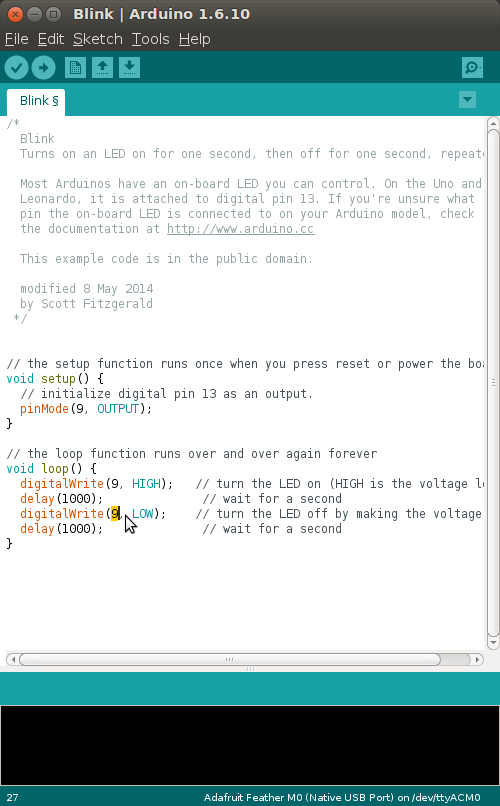
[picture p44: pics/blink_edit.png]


- Change the 'delay' rate to 500 milliseconds (or something significantly different from 1000 milliseconds, which is the blinking rate that the Riffle comes pre-programmed to display).

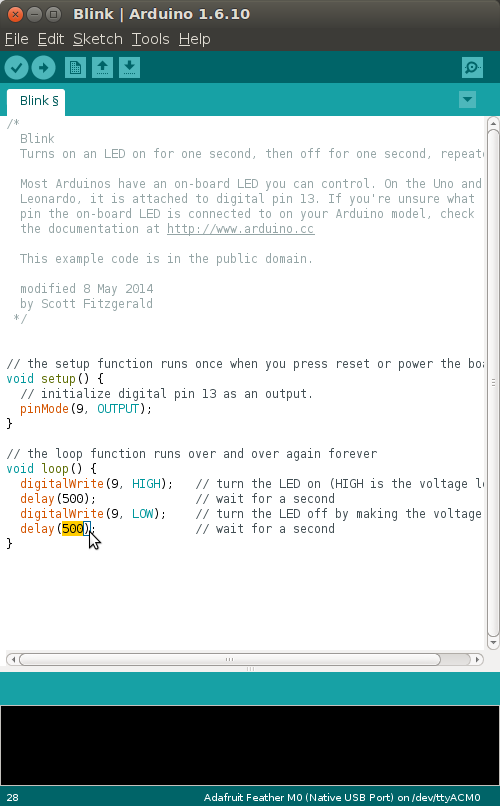
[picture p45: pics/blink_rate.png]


- Compile and load the code using the 'right arrow' button:

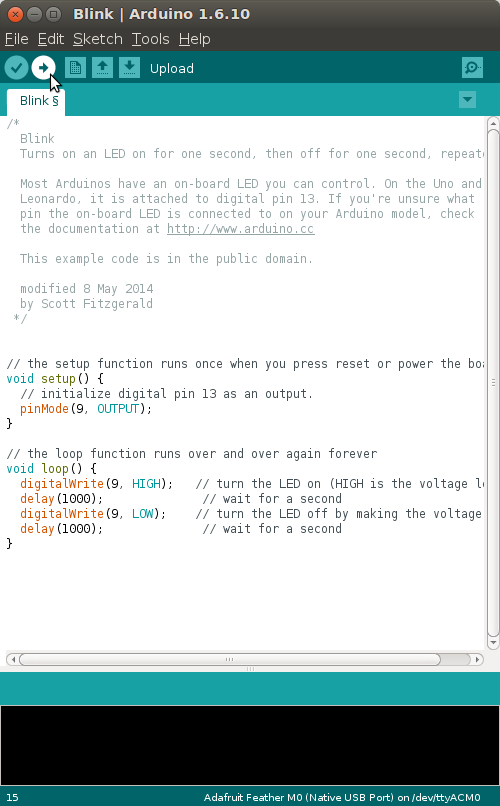
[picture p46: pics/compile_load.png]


- After the code has uploaded, you should see that the blink rate on the Riffle has changed to the blink rate you have programmed it to.

# Basic datalogging

### Prepare the hardware

- Insert a Lithium-Ion battery into the 'USB/Lith' JST port.

- Insert a CR1220 coin battery into the coin battery slot.

- Insert a microUSB card into the microUSB slot.

- Make sure your Riffle is connected to your computer via USB, and that the power switch is turned to "USB/Lith'.

### Install the necessary Arduino libraries

-  In order to get the Arduino libraries needed to run the example datalogging code, it's easiest to download the entire contents of [this](https://github.com/dwblair/Riffle-Getting-Started/) github repository by clicking on "Clone/download".  

- Create a new folder on your computer for the files that are unzipped from this repository, and copy the files into that folder.

- Find out where your Arduino 'sketchbook' folder is.  You can do this by going to File: Preferences, 

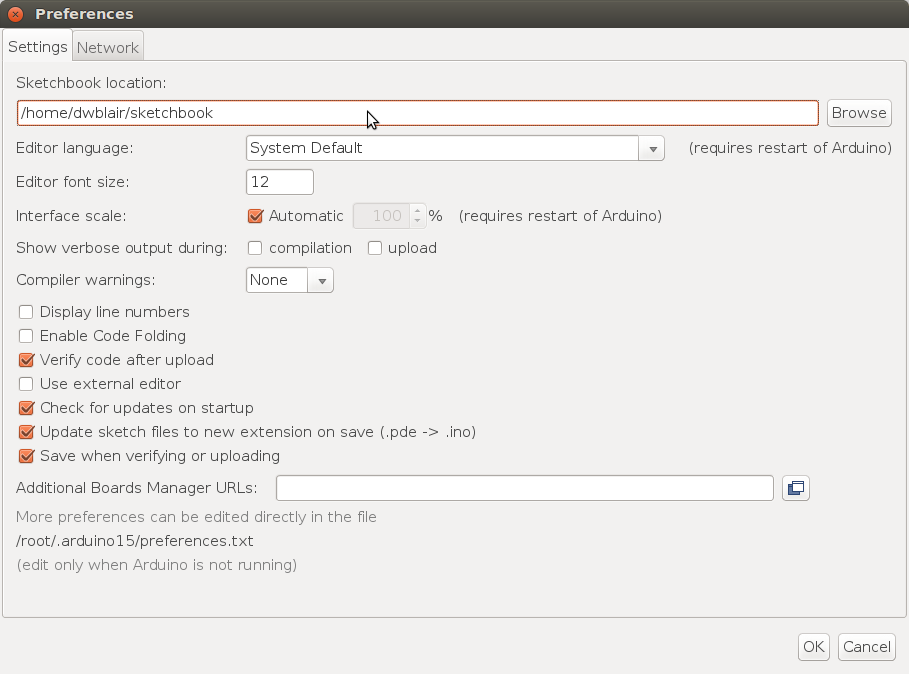
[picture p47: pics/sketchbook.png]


- In your sketchbook folder, create a folder named 'libraries'.

- Drag all of the folders in the "arduino_libraries" folder you downloaded from github into your 'libraries' folder.

- Close and re-open the Arduino IDE.

- Use 'File: Open' to open the 'temp_logger.ino' sketch.

- Compile and load the sketch onto the Arduino.

- [MORE DETAIL RE: WHAT TO EXPECT FROM DATALOGGER FILE HERE -- pending finalized temp_logger.ino code]

### Notes on datalogging

- The code of temp_logger.ino sets the real time clock (RTC) time to your computer system's time every time the Arduino IDE uploads to the Riffle. This time should then persist as long as the CR1220 battery is powering the RTC (whether or not there is another power source for the Riffle).

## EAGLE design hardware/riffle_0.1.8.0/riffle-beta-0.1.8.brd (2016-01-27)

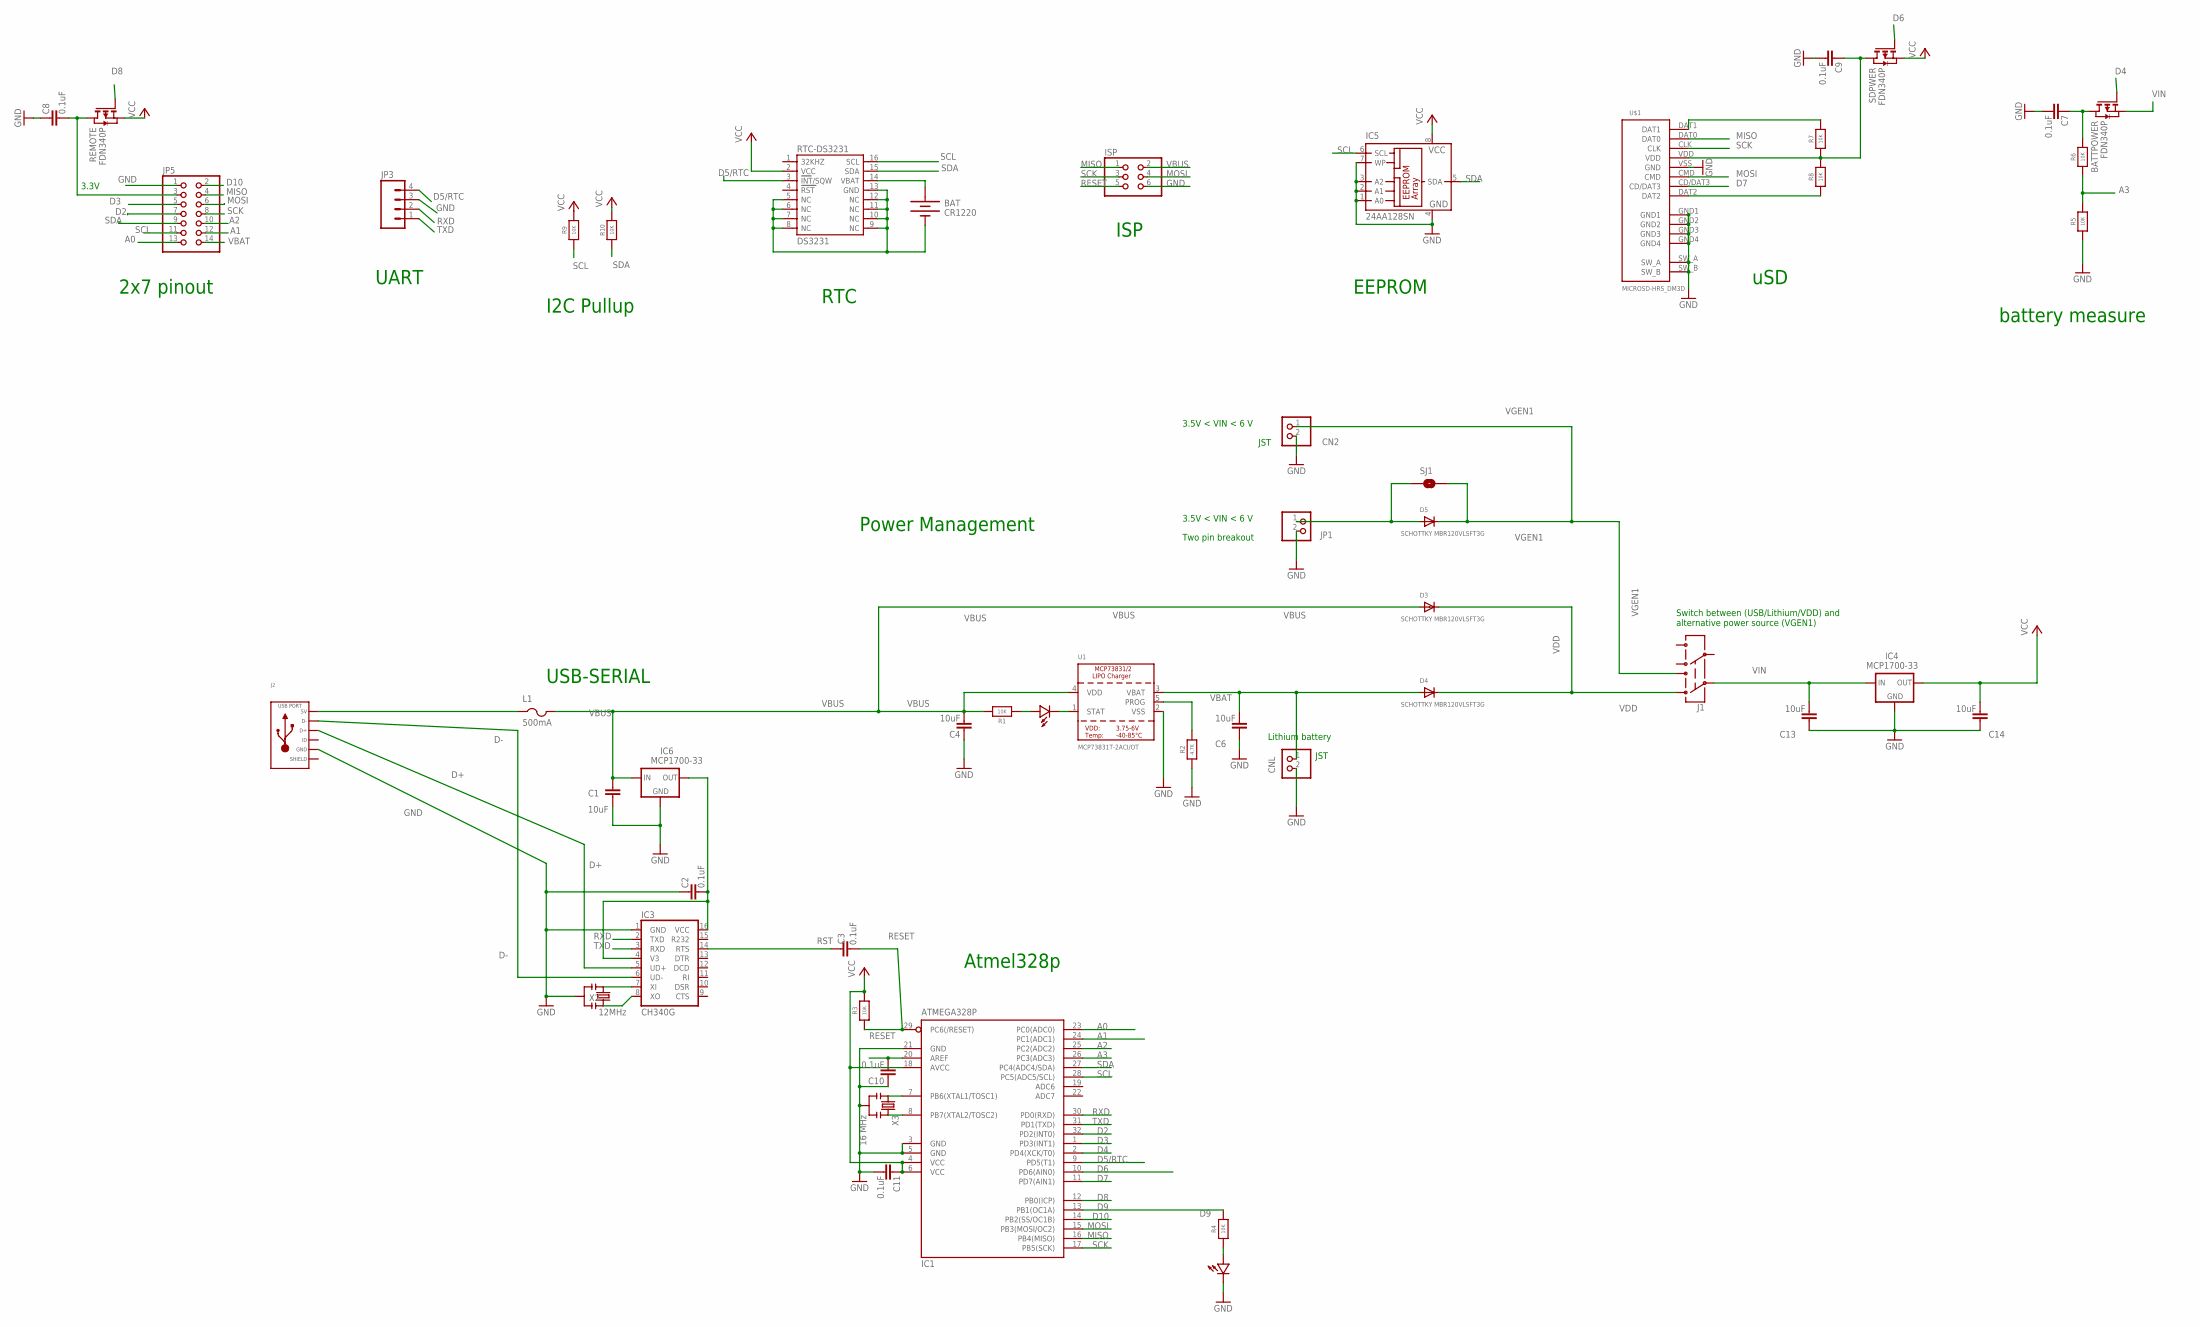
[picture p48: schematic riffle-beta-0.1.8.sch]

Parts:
BAT: CR1220; BATTCON_12MM_SMT
BATTPOWER: FDN340P; SOT-23
C1, C4, C6, C13, C14: 10uF; 0603-CAP
C2, C3, C7, C8, C9, C10, C11: 0.1uF; 0603-CAP
CN2: JST_2PIN-SMT-RA; JST-PH-2-SMT-RA
CNL: JST_2PIN-SMT-RA; JST-PH-2-SMT-RA
D1, D2: LED0603; 0603-LED
D3, D4, D5: SCHOTTKY MBR120VLSFT3G; SOD-123FL
IC1: ATMEGA328P; TQFP32-08
IC3: CH340G; SO16
IC4, IC6: MCP1700-33; SOT89
IC5: 24AA128SN; SO-08
ISP: PINHD-2X3; 2X03
J1: AYZ0202
J2: USB_MICRO_RIGHT; MICROUSB-RIGHT
JP1: PINHD-1X2; 1X02
JP3: M04SMD; 1X04-SMD
JP5: PINHD-2X7; 2X07
L1: 500mA; R1206
R1, R3, R4, R5, R6, R7, R8, R9, R10: 10K; 0603-NO
R2: 4.7K; 0603-NO
REMOTE: FDN340P; SOT-23
RTC-DS3231: DS3231
SDPWER: FDN340P; SOT-23
SJ1: SOLDERJUMPERNO; SJ_2S-NO
U1: MCP73831T-2ACI/OT; SOT23-5
U$1: MICROSD-HRS_DM3D; DM3D
X2: 12MHz; RESONATOR-SMD
X3: 16 MHz; RESONATOR-SMD

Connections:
A0: IC1.23 (PC0(ADC0)), JP5.13
A1: IC1.24 (PC1(ADC1)), JP5.12
A2: IC1.25 (PC2(ADC2)), JP5.10
A3: IC1.26 (PC3(ADC3)), R5.2, R6.1
AREF: C10.1, IC1.20 (AREF)
D2: IC1.32 (PD2(INT0)), JP5.7
D3: IC1.1 (PD3(INT1)), JP5.5
D4: BATTPOWER.3 (G), IC1.2 (PD4(XCK/T0))
D5/RTC: IC1.9 (PD5(T1)), JP3.4, RTC-DS3231.3 (INT/SQW)
D6: IC1.10 (PD6(AIN0)), SDPWER.3 (G)
D7: IC1.11 (PD7(AIN1)), U$1.CD/DAT3
D8: IC1.12 (PB0(ICP)), REMOTE.3 (G)
D9: IC1.13 (PB1(OC1A)), R4.2
D10: IC1.14 (PB2(SS/OC1B)), JP5.2
D+: IC3.5 (UD+), J2.3 (D+)
D-: IC3.6 (UD-), J2.2 (D-)
GND: BAT.P$1 (-), C1.1, C2.2, C4.2, C6.2, C7.1, C8.2, C9.1, C10.2, C11.1, C13.2, C14.2, CN2.2 (1), CNL.2 (1), D2.MINUS, IC1.3 (GND), IC1.5 (GND), IC1.21 (GND), IC3.1 (GND), IC4.1 (GND), IC5.1 (A0), IC5.2 (A1), IC5.3 (A2), IC5.4 (GND), IC5.7 (WP), IC6.1 (GND), ISP.6, J2.5 (GND), JP1.2, JP3.3, JP5.1, R2.1, R5.1, RTC-DS3231.5 (NC), RTC-DS3231.6 (NC), RTC-DS3231.7 (NC), RTC-DS3231.8 (NC), RTC-DS3231.9 (NC), RTC-DS3231.10 (NC), RTC-DS3231.11 (NC), RTC-DS3231.12 (NC), RTC-DS3231.13 (GND), U1.2 (VSS), U$1.GND1, U$1.GND2, U$1.GND3, U$1.GND4, U$1.SW_A, U$1.SW_B, U$1.VSS (GND), X2.2, X3.2
MISO: IC1.16 (PB4(MISO)), ISP.1, JP5.4, U$1.DAT0
MOSI: IC1.15 (PB3(MOSI/OC2)), ISP.4, JP5.6, U$1.CMD
unnamed: IC1.7 (PB6(XTAL1/TOSC1)), X3.1
unnamed: IC1.8 (PB7(XTAL2/TOSC2)), X3.3
unnamed: C9.2, R7.1, R8.2, SDPWER.1 (D), U$1.VDD
unnamed: D1.MINUS, U1.1 (STAT)
unnamed: R2.2, U1.5 (PROG)
unnamed: C8.1, JP5.3, REMOTE.1 (D)
unnamed: C2.1, IC3.4 (V3), IC3.16 (VCC), IC6.3 (OUT)
unnamed: J2.1 (5V), L1.1
unnamed: D5.A, JP1.1, SJ1.1
unnamed: IC3.7 (XI), X2.1
unnamed: IC3.8 (XO), X2.3
unnamed: BATTPOWER.1 (D), C7.2, R6.2
unnamed: R7.2, U$1.DAT1
unnamed: D2.PLUS, R4.1
unnamed: R8.1, U$1.DAT2
unnamed: D1.PLUS, R1.1
RESET: C3.1, IC1.29 (PC6(/RESET)), ISP.5, R3.1
RST: C3.2, IC3.14 (RTS)
RTC_BATT: BAT.P$2 (+), RTC-DS3231.14 (VBAT)
RXD: IC1.30 (PD0(RXD)), IC3.2 (TXD), JP3.2
SCK: IC1.17 (PB5(SCK)), ISP.3, JP5.8, U$1.CLK
SCL: IC1.28 (PC5(ADC5/SCL)), IC5.6 (SCL), JP5.11, R9.1, RTC-DS3231.16 (SCL)
SDA: IC1.27 (PC4(ADC4/SDA)), IC5.5 (SDA), JP5.9, R10.1, RTC-DS3231.15 (SDA)
SLD: J2.S1 (SLD), J2.S2 (SLD), J2.S3 (SLD), J2.S4 (SLD), J2.S5 (SLD), J2.S6 (SLD), J2.S7 (SLD), J2.S8 (SLD)
TXD: IC1.31 (PD1(TXD)), IC3.3 (RXD), JP3.1
VBAT: C6.1, CNL.1 (2), D4.A, JP5.14, U1.3 (VBAT)
VBUS: C1.2, C4.1, D3.A, IC6.2 (IN), ISP.2, L1.2, R1.2, U1.4 (VDD)
VCC: C11.2, C14.1, IC1.4 (VCC), IC1.6 (VCC), IC1.18 (AVCC), IC4.3 (OUT), IC5.8 (VCC), R3.2, R9.2, R10.2, REMOTE.2 (S), RTC-DS3231.2 (VCC), SDPWER.2 (S)
VDD: D3.C, D4.C, J1.3 (1)
VGEN1: CN2.1 (2), D5.C, J1.1 (3), SJ1.2
VIN: BATTPOWER.2 (S), C13.1, IC4.2 (IN), J1.2

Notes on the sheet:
3.3V
USB-SERIAL
Atmel328p
Power Management
RTC
uSD
2x7 pinout
UART
I2C Pullup
ISP
EEPROM
battery measure
Lithium battery
3.5V < VIN < 6 V
JST
Two pin breakout
Switch between (USB/Lithium/VDD) and alternative power source (VGEN1)

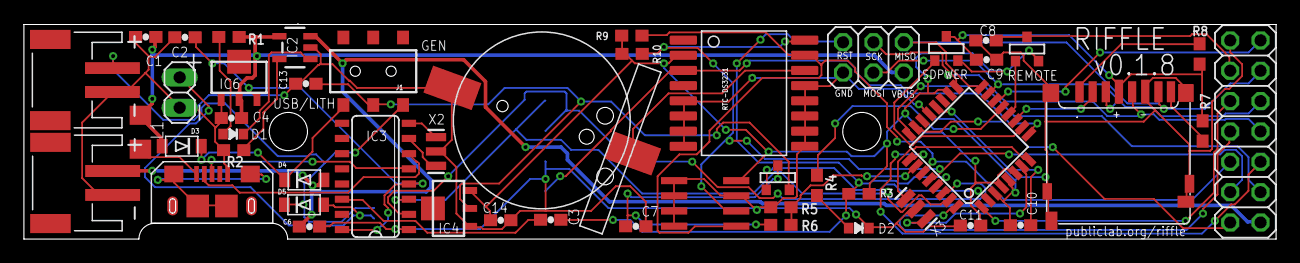
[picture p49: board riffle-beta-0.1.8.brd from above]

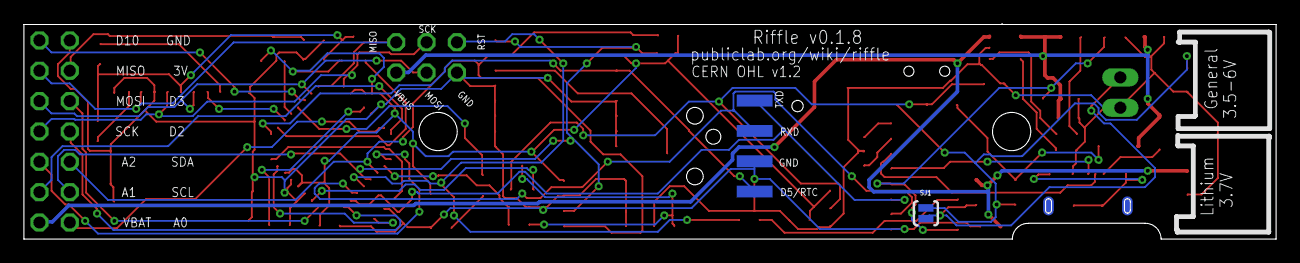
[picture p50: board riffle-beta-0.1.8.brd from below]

Board: 2 copper layers, 104.8 x 18.0 mm, 51 parts (2 on the bottom side), 50 nets.

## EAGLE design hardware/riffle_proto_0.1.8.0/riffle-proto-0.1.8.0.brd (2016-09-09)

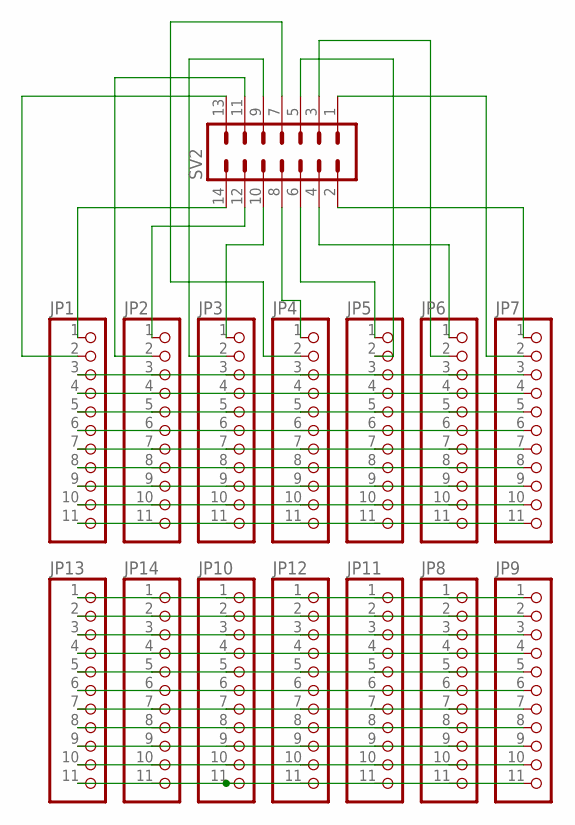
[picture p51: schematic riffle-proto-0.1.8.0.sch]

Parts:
JP1, JP2, JP3, JP4, JP5, JP6, JP7, JP8, JP9, JP10, JP11, JP12, JP13, JP14: HEADER-1X1176MIL; 1X11_ROUND_76
SV2: MA07-2

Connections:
unnamed: JP1.1, SV2.14
unnamed: JP2.1, SV2.12
unnamed: JP3.1, SV2.10
unnamed: JP4.1, SV2.8
unnamed: JP5.1, SV2.6
unnamed: JP6.1, SV2.4
unnamed: JP7.1, SV2.2
unnamed: JP1.2, SV2.13
unnamed: JP2.2, SV2.11
unnamed: JP3.2, SV2.9
unnamed: JP4.2, SV2.7
unnamed: JP5.2, SV2.5
unnamed: JP6.2, SV2.3
unnamed: JP7.2, SV2.1
unnamed: JP1.3, JP2.3, JP3.3, JP4.3, JP5.3, JP6.3, JP7.3
unnamed: JP1.4, JP2.4, JP3.4, JP4.4, JP5.4, JP6.4, JP7.4
unnamed: JP1.5, JP2.5, JP3.5, JP4.5, JP5.5, JP6.5, JP7.5
unnamed: JP1.6, JP2.6, JP3.6, JP4.6, JP5.6, JP6.6, JP7.6
unnamed: JP1.7, JP2.7, JP3.7, JP4.7, JP5.7, JP6.7, JP7.7
unnamed: JP1.8, JP2.8, JP3.8, JP4.8, JP5.8, JP6.8, JP7.8
unnamed: JP1.9, JP2.9, JP3.9, JP4.9, JP5.9, JP6.9, JP7.9
unnamed: JP1.10, JP2.10, JP3.10, JP4.10, JP5.10, JP6.10, JP7.10
unnamed: JP1.11, JP2.11, JP4.11, JP5.11, JP6.11, JP7.11
unnamed: JP8.1, JP9.1, JP10.1, JP11.1, JP12.1, JP13.1, JP14.1
unnamed: JP8.2, JP9.2, JP10.2, JP11.2, JP12.2, JP13.2, JP14.2
unnamed: JP8.3, JP9.3, JP10.3, JP11.3, JP12.3, JP13.3, JP14.3
unnamed: JP8.4, JP9.4, JP10.4, JP11.4, JP12.4, JP13.4, JP14.4
unnamed: JP8.5, JP9.5, JP10.5, JP11.5, JP12.5, JP13.5, JP14.5
unnamed: JP8.6, JP9.6, JP10.6, JP11.6, JP12.6, JP13.6, JP14.6
unnamed: JP8.7, JP9.7, JP10.7, JP11.7, JP12.7, JP13.7, JP14.7
unnamed: JP8.8, JP9.8, JP10.8, JP11.8, JP12.8, JP13.8, JP14.8
unnamed: JP8.9, JP9.9, JP10.9, JP11.9, JP12.9, JP13.9, JP14.9
unnamed: JP8.10, JP9.10, JP10.10, JP11.10, JP12.10, JP13.10, JP14.10
unnamed: JP8.11, JP9.11, JP10.11, JP11.11, JP12.11, JP13.11, JP14.11

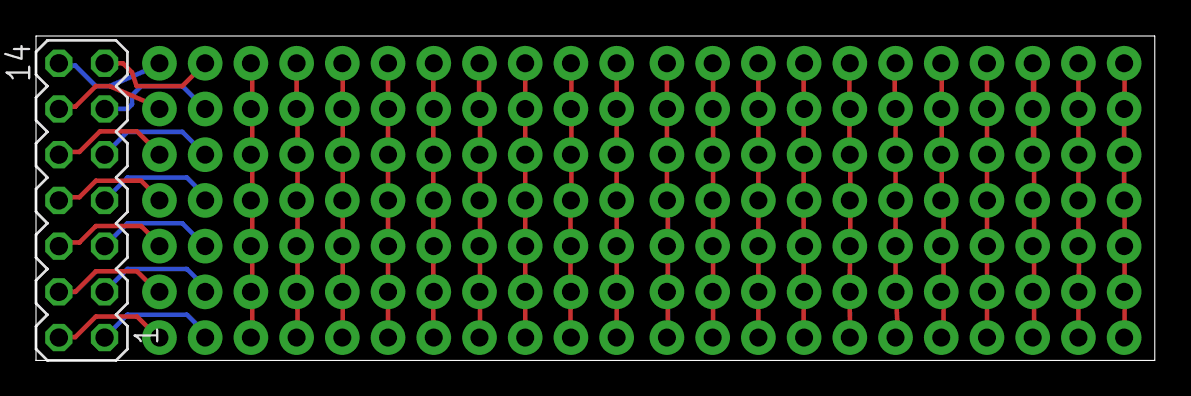
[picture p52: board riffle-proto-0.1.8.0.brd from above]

Board: 2 copper layers, 62.2 x 18.0 mm, 15 parts (0 on the bottom side), 34 nets.

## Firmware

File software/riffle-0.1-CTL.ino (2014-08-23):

#include <JeeLib.h>
#include <Wire.h>
#include <SPI.h>
#include <SD.h>
#include <RTClib.h>
#include <RTC_DS3231.h>
#include<stdlib.h>

#define led 6 //indicator led
#define photocellPin A2

#define debug 1 //whether or not to print statements out on serial

//sleeping
ISR(WDT_vect) { Sleepy::watchdogEvent(); }
#define LOG_INTERVAL_BASE  1000 // in millisec -- 60000 (60 sec) max 
#define LOG_INTERVAL_REPEAT 10 // number of times to repeat BASE

//battery
#define BATTERYPIN A3

//RTC
RTC_DS3231 RTC;

//sd card and filename
const int chipSelect = 7;    
int SDpower = 5;
int sensorPower = 4;

char filename[] = "LOGGER00.csv";
File dataFile;
String fileHeader = "DATETIME,RTC_TEMP_C,TEMP_C,CONDUCT_FREQ_HERTZ,BATTERY_LEVEL";


// temp variables 

// which analog pin to connect
#define THERMISTORPIN A0         
// resistance at 25 degrees C
#define THERMISTORNOMINAL 10000      
// temp. for nominal resistance (almost always 25 C)
#define TEMPERATURENOMINAL 25   
// how many samples to take and average, more takes longer
// but is more 'smooth'
#define NUMSAMPLES 5
// The beta coefficient of the thermistor (usually 3000-4000)
#define BCOEFFICIENT 3950
// the value of the 'other' resistor
#define SERIESRESISTOR 9550

int samples[NUMSAMPLES];

int interruptPin = 0; //corresponds to D2

// conductivity variables

long pulseCount = 0;  //a pulse counter variable

unsigned long pulseTime,lastTime, duration, totalDuration;

int samplingPeriod=2; // the number of seconds to measure 555 oscillations

int sensorBoard = A1; // the pin that powers the 555 subcircuit

void setup()
{
   if (debug==1){
    Serial.begin(9600);
  } 
  
      pinMode(sensorBoard, OUTPUT);   
      pinMode(THERMISTORPIN, INPUT);
      pinMode(led, OUTPUT);     
      
      //turn on SD card
      pinMode(SDpower,OUTPUT);
      //pinMode(sensorPower,OUTPUT); -- doesn't work on REVC, will work on REVD
      digitalWrite(SDpower,LOW);
      
      //initialize the SD card  
  if (debug==1){
    Serial.println();
    Serial.print("Initializing SD card...");
  }
  pinMode(SS, OUTPUT);
  
  // see if the card is present and can be initialized:
  if (!SD.begin(chipSelect)) {  

     if (debug==1){
      Serial.println("Card failed, or not present");
    }
      
    for (int j=0;j<100;j++) {
        digitalWrite(led, LOW);
        delay(100);
        digitalWrite(led, HIGH);
         delay(100);
  }
  digitalWrite(led, LOW);
  
   
    // don't do anything more:
    while (1) ;
  }

  if (debug==1) {
    Serial.println("card initialized.");
  }
  
  for (uint8_t i = 0; i < 100; i++) {
    filename[6] = i/10 + '0';
    filename[7] = i%10 + '0';
    if (! SD.exists(filename)) {
      // only open a new file if it doesn't exist
      if (debug==1) {
        Serial.print("Writing to file: " );
        Serial.println(filename);
      }
      dataFile = SD.open(filename, FILE_WRITE);
      dataFile.println(fileHeader);
      dataFile.close();
      break;  // leave the loop!
    }
  }  
      
     // for i2c for RTC
  Wire.begin();
  RTC.begin();   
      
    // check on the RTC
  if (! RTC.isrunning()) {
    if (debug==1){
      Serial.println("RTC is NOT running!");
    }
      // following line sets the RTC to the date & time this sketch was compiled
    RTC.adjust(DateTime(__DATE__, __TIME__));
  }
  
  DateTime now = RTC.now();
  DateTime compiled = DateTime(__DATE__, __TIME__);
  if (now.unixtime() < compiled.unixtime()) {
    if (debug==1) {
    Serial.println("RTC is older than compile time! Updating");
    }
    RTC.adjust(DateTime(__DATE__, __TIME__));
  }
  if (debug==1) {
  Serial.println();
  Serial.println(fileHeader);  
  }
      
      
  //show that we're working
  if (debug==0) {
  for (int j=0;j<4;j++) {
  digitalWrite(led, LOW);
  delay(1000);
  digitalWrite(led, HIGH);
   delay(1000);
  }
  
   for (int j=0;j<3;j++) {
  digitalWrite(led, LOW);
  delay(500);
  digitalWrite(led, HIGH);
   delay(500);
  }
  
   digitalWrite(led, LOW);
   delay(1000);    
  }    
      
}

void loop()
{
   uint8_t i;
  float average;
  
  
  //turn on the sensorBoard system
  digitalWrite(sensorBoard,HIGH); //turns on the 555 timer subcircuit
  
  
  // temperature ---------------------------------------------
 
 
  // take N samples in a row, with a slight delay
  for (i=0; i< NUMSAMPLES; i++) {
   samples[i] = analogRead(THERMISTORPIN);
   //Serial.println(analogRead(THERMISTORPIN));
   delay(10);
  }
  
  // conductivity --------------------------------------
  
  pulseCount=0; //reset the pulse counter
  totalDuration=0;  //reset the totalDuration of all pulses measured
  
  attachInterrupt(interruptPin,onPulse,RISING); //attach an interrupt counter to interrupt pin 1 (digital pin #3) -- the only other possible pin on the 328p is interrupt pin #0 (digital pin #2)
  
  pulseTime=micros(); // start the stopwatch
  
  delay(samplingPeriod*1000); //give ourselves samplingPeriod seconds to make this measurement, during which the "onPulse" function will count up all the pulses, and sum the total time they took as 'totalDuration' 
 
  detachInterrupt(interruptPin); //we've finished sampling, so detach the interrupt function -- don't count any more pulses
  
  
  // get the photodiode reading
  int photocellReading;
  photocellReading = analogRead(photocellPin); 
  
  //turn off the sensorBoard system
  digitalWrite(sensorBoard,LOW); //turns on the 555 timer and thermistor subcircuit
  
  
  // average all the samples out
  average = 0;
  for (i=0; i< NUMSAMPLES; i++) {
     average += samples[i];
  }
  average /= NUMSAMPLES;
 
  // convert the value to resistance
  average = 1023 / average - 1;
  average = SERIESRESISTOR / average;
  //Serial.print("Thermistor resistance "); 
  //Serial.println(average);
 
  float steinhart;
  steinhart = average / THERMISTORNOMINAL;     // (R/Ro)
  steinhart = log(steinhart);                  // ln(R/Ro)
  steinhart /= BCOEFFICIENT;                   // 1/B * ln(R/Ro)
  steinhart += 1.0 / (TEMPERATURENOMINAL + 273.15); // + (1/To)
  steinhart = 1.0 / steinhart;                 // Invert
  steinhart -= 273.15;                         // convert to C
 
  //Serial.print(steinhart);
  //Serial.println(" *C");
  
 
  //do the conductivity calculations
  
  double freqHertz;
  if (pulseCount>0) { //use this logic in case something went wrong
  
  double durationS=(totalDuration/double(pulseCount))/1000000.; //the total duration, in seconds, per pulse (note that totalDuration was in microseconds)
  freqHertz=1./durationS;
  }
  else {
    freqHertz=0.;
  }
  
  // Onboard temp from the RTC
  float rtcTemp = RTC.getTempAsFloat();
  
  //get the time
  DateTime now = RTC.now();
  long unixNow = now.unixtime();
  
  // Get the battery level
  int batteryLevel = analogRead(BATTERYPIN);
  
  
  
  // make a string for assembling the data to log:
  String dataString = "";
  
  // dataString += String(unixNow);
  dataString += now.unixtime();
  dataString += ",";
  dataString += now.year();
  dataString += "-";
  dataString += padInt(now.month(), 2);
  dataString += "-";
  dataString += padInt(now.day(), 2);
  dataString += " ";
  dataString += padInt(now.hour(), 2);
  dataString += ":";
  dataString += padInt(now.minute(), 2);
  dataString += ":";
  dataString += padInt(now.second(), 2);
  dataString += ",";
  char buffer[10];
  dataString += dtostrf(rtcTemp, 5, 2, buffer);
  dataString += ",";
  dataString += dtostrf(steinhart,5,2,buffer);
  dataString += ",";
  dataString += dtostrf(freqHertz,6,2,buffer);
  dataString += ",";
  dataString += String(photocellReading);
  dataString += ",";
  dataString += String(batteryLevel);

  
  // Open up the file we're going to log to!
  dataFile = SD.open(filename, FILE_WRITE);
  if (!dataFile) {
    if (debug==1){
      Serial.print("Error opening file:");
      Serial.println(filename);
    }
    
    // Wait forever since we cant write data
    while (1) ;
  }
  
   digitalWrite(led, HIGH);
  delay(30);
  
  // Write the string to the card
  dataFile.println(dataString);
  dataFile.close();
  
  digitalWrite(led,LOW);
  
  if (debug==1) {
    Serial.println(dataString);
  }
  
// go to sleep!
   
     if (debug==0) {
       for (int k=0;k<LOG_INTERVAL_REPEAT;k++) {
    Sleepy::loseSomeTime(LOG_INTERVAL_BASE); //-- will interfere with serial, so don't use when debugging 
       }
  } else {
    delay (LOG_INTERVAL_BASE); // use when debugging -- loseSomeTime does goofy things w/ serial
  }
  
   
  
}
  
String padInt(int x, int pad) {
  String strInt = String(x);
  
  String str = "";
  
  if (strInt.length() >= pad) {
    return strInt;
  }
  
  for (int i=0; i < (pad-strInt.length()); i++) {
    str += "0";
  }
  
  str += strInt;
  
  return str;
}

String int2string(int x) {
  // formats an integer as a string assuming x is in 1/100ths
  String str = String(x);
  int strLen = str.length();
  if (strLen <= 2) {
    str = "0." + str;
  } else if (strLen <= 3) {
    str = str.substring(0, 1) + "." + str.substring(1);
  } else if (strLen <= 4) {
    str = str.substring(0, 2) + "." + str.substring(2);
  } else {
    str = "-9999";
  }
  
  return str;
}

void onPulse()
{
  pulseCount++;
  //Serial.print("pulsecount=");
  //Serial.println(pulseCount);
  lastTime = pulseTime;
  pulseTime = micros();
  duration=pulseTime-lastTime;
  totalDuration+=duration;
  //Serial.println(totalDuration);
}

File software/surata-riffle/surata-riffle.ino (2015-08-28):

nclude <JeeLib.h>
#include <Wire.h>
#include <SPI.h>
#include <RTClib.h>
#include <RTC_DS3231.h>
#include<stdlib.h>
#include <SD.h>

//sleeping stuff
ISR(WDT_vect) { Sleepy::watchdogEvent(); }

//RTC stuff
RTC_DS3231 RTC;

//led
#define led 9

//battery stuff
#define batteryAnalogMeasurePin A3
#define batteryReadCircuitSwitch 4


// which analog pin to connect
#define THERMISTORPIN A0         
// resistance at 25 degrees C
#define THERMISTORNOMINAL 10000      
// temp. for nominal resistance (almost always 25 C)
#define TEMPERATURENOMINAL 25   
// how many samples to take and average, more takes longer
// but is more 'smooth'
#define NUMSAMPLES 5
// The beta coefficient of the thermistor (usually 3000-4000)
#define BCOEFFICIENT 3950
// the value of the 'other' resistor
#define SERIESRESISTOR 9550


// debugging -- only do Serial output if debuggin
#define debug 1 // 0: don't print anything out; 1: print out debugging statements

// how long to sleep between measurements
#define sleepSeconds 3

int samples[NUMSAMPLES];

int interruptPin = 1; //corresponds to D2

// conductivity variables

long pulseCount = 0;  //a pulse counter variable

unsigned long pulseTime,lastTime, duration, totalDuration;

int samplingPeriod=3; // the number of seconds to measure 555 oscillations

int sensorBoard = 8; // the pin that powers the 555 subcircuit

const int chipSelect = 7;
int SDpower = 6;


void setup() {
  
  pinMode(SDpower,OUTPUT);
    digitalWrite(SDpower,LOW);
    
     if (!SD.begin(chipSelect)) {
  //  Serial.println("Card failed, or not present");
    // don't do anything more:
    for (int j=0;j<20;j++) {
      digitalWrite(led,HIGH);
      delay(10);
      digitalWrite(led,LOW);
      
    }
  }
  
  if (debug) Serial.begin(115200);
  
  // begin I2C protocol (necessary for RTC, and any other I2C on board
  Wire.begin();

  // RTC -------------------------
  initialize_RTC(); // NOTE: need to initialize I2C first -- but also for any other I2C library
  
  // set mode for battery circuit control pin, and turn the circuit off
  pinMode(batteryReadCircuitSwitch,OUTPUT);
  pinMode(sensorBoard,OUTPUT);
  digitalWrite(batteryReadCircuitSwitch, HIGH);
  
  pinMode(led, OUTPUT);     

pinMode(sensorBoard,OUTPUT); //turns on the 555 timer and thermistor subcircuit
  digitalWrite(sensorBoard,LOW); //turns on the 555 timer and thermistor subcircuit

}

void loop () {
  
  uint8_t i;
  
  //measure the battery 
  digitalWrite(batteryReadCircuitSwitch, LOW); //turn on battery measurement circuit
  int batteryLevel = analogRead(batteryAnalogMeasurePin);
  digitalWrite(batteryReadCircuitSwitch, HIGH);
 
 
 //turn on the sensorBoard system
  
 //measure temp 
 
 //take temp samples
 // take N samples in a row, with a slight delay
 for (i=0; i< NUMSAMPLES; i++) {
   samples[i] = analogRead(THERMISTORPIN);
   //Serial.println(analogRead(THERMISTORPIN));
   delay(10);
  }
  
  //measure conductivity
  // conductivity --------------------------------------
  
  pulseCount=0; //reset the pulse counter
  totalDuration=0;  //reset the totalDuration of all pulses measured
  
  attachInterrupt(interruptPin,onPulse,RISING); //attach an interrupt counter to interrupt pin 1 (digital pin #3) -- the only other possible pin on the 328p is interrupt pin #0 (digital pin #2)
  
  pulseTime=micros(); // start the stopwatch
  
  delay(samplingPeriod*1000); //give ourselves samplingPeriod seconds to make this measurement, during which the "onPulse" function will count up all the pulses, and sum the total time they took as 'totalDuration' 
 
  detachInterrupt(interruptPin); //we've finished sampling, so detach the interrupt function -- don't count any more pulses
  
  
  //turn off the remote board
  
//digitalWrite(sensorBoard,HIGH); //turns on the 555 timer and thermistor subcircuit
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

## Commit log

2016-01-07 fixed IC2 footprint from 6 to 5 pins
    [riffle-beta-0.1.3.brd]
2016-01-12 tightened USB cutout; moved via away from left screw
    [riffle-beta-0.1.3.brd, riffle-beta-0.1.3.sch]
2016-01-12 added +/- artwork
    [riffle-beta-0.1.3.brd]
2016-01-23 fixed switch; added diodes
    [riffle-beta-0.1.4.brd, riffle-beta-0.1.4.sch]
2016-01-23 cleaned up schematic
    [riffle-beta-0.1.4.sch]
2016-01-23 routed board
    [riffle-beta-0.1.4.brd]
2016-01-23 added fuse and VBUS diode
    [riffle-beta-0.1.3.2.brd, riffle-beta-0.1.3.2.sch]

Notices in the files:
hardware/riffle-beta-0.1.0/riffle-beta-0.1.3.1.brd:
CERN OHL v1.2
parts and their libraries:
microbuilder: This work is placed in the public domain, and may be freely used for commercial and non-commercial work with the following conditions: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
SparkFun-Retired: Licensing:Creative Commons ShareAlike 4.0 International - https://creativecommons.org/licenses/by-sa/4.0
